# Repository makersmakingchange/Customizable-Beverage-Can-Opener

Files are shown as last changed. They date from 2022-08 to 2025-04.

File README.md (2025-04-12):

# Customizable Beverage Can Opener
The Customizable Beverage Can Opener is a beverage opening tool with different handle options for users with low strength and accuracy.

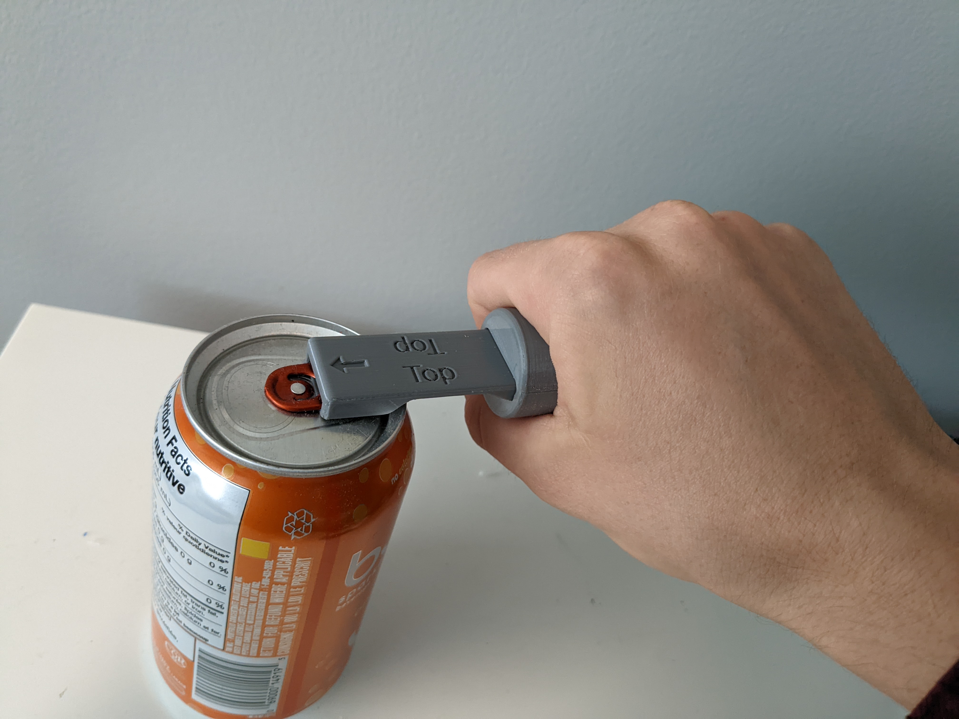
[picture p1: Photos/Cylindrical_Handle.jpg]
Picture of Customizable Beverage Can Opener.


## More info at
- [Makers Making Change Project Page](https://makersmakingchange.com/project/customizable-beverage-can-opener/)

## How to Obtain a Customizable Beverage Can Opener
### 1. Do it Yourself (DIY) or Do it Together (DIT)

This is an open-source assistive technology, so anyone is free to build it. All of the files and instructions required to build the Customizable Beverage Can Opener are contained within this repository. Refer to the Maker Checklist below.

### 2. Request a build of this device

If you would like to obtain a Customizable Beverage Can Opener, you may submit a build request through the [MMC Library Page](https://makersmakingchange.com/project/customizable-beverage-can-opener). The requestor is responsible for the cost of materials and any shipping.

### 3. How to build this device for someone else

If you have the skills and equipment to build this device, and would like to donate your time to create the switch for someone who needs it, visit the [MMC Maker Wanted](https://makersmakingchange.com/maker-wanted/) section.

## Getting Started

### 1. Read the Makers Checklist

The [Makers Checklist](Documentation/Customizable_Beverage_Can_Opener_Maker_Checklist_v1.0.pdf).

### 2. Print the 3D Printable components

Print the Base Can Opener and, optionally, any of the three handle designs.

All of the files and individual print files can be in the [/Build_Files/3D_Printing_Files](/Build_Files/3D_Printing_Files) folder.

### 3. Assemble the Customizable Berage Can Opener

Reference the [User Quick Guide](Documentation/Customizable_Beverage_Can_Opener_User_Guide_v1.0.pdf) for the tools and steps required to build each portion.

## Files
### Documentation
| Document             | Version | Link |
|----------------------|---------|------|
| Design Rationale     | 1.0     | [Customizable_Beverage_Can_Opener_Design_Rationale](/Documentation/Customizable_Beverage_Can_Opener_Design_Rationale_v1.0.pdf)     |
| Maker Checklist      | 1.0     | [Customizable_Beverage_Can_Opener_Maker_Checklist](/Documentation/Customizable_Beverage_Can_Opener_Maker_Checklist_v1.0.pdf)     |
| Bill of Materials    | 1.0     | [Customizable_Beverage_Can_Opener_Bill_of_Materials](/Documentation/Customizable_Beverage_Can_Opener_BOM_v1.0.csv)     |
| 3D Printing Guide    | 1.0     | [Customizable_Beverage_Can_Opener_3D_Printing_Guide](/Documentation/Customizable_Beverage_Can_Opener_3D_Print_Guide_v1.0.pdf)     |
| User Guide           | 1.0     | [Customizable_Beverage_Can_Opener_User_Guide](/Documentation/Customizable_Beverage_Can_Opener_User_Guide_v1.0.pdf)    |
| Changelog            | 1.0     | [Customizable_Beverage_Can_Opener_Changelog](/Documentation/Customizable_Beverage_Can_Opener_Changelog_v1.0.pdf)     |

### Design Files
[CAD Files](/Design_Files)

### Build Files
 - [3D Printing Files](/Build_Files/3D_Printing_Files)

## Attribution
Designers:
 - Idea for base can opener based on the design of pop-top can opener by Thingiverse User VegasGuy under the Creative Commons license - Attribution - Non-Commercial - No Derivatives.
 - Idea for Flat Handle based on Can Opener Helper by Pole Ergo under the Creative Commons license - Attribution - Non-Commercial - No Derivative.
 - Full Design by Neil Squire / Makers Making Change under license.
 - Documentation by Neil Squire / Makers Making Change.

## License
Everything needed or used to design, make, test, or prepare the Customizable Beverage Can Opener is licensed under the CERN 2.0 Permissive license <https://ohwr.org/project/cernohl/wikis/Documents/CERN-OHL-version-2> (CERN-OHL-P). 

<br /><span xmlns:dct="http://purl.org/dc/terms/" property="dct:title"><Device-Name></span> by <a xmlns:cc="http://creativecommons.org/ns#" href="www.makersmakingchange.com" property="cc:attributionName" rel="cc:attributionURL">Neil Squire</a> is licensed under a <a rel="license" href="http://creativecommons.org/licenses/by-sa/4.0/">Creative Commons Attribution-ShareAlike 4.0 International License</a>.

<!-- ABOUT MMC START -->
## About Makers Making Change
[Makers Making Change Logo](https://www.makersmakingchange.com/)

Makers Making Change is a program of [Neil Squire](https://www.neilsquire.ca/), a Canadian non-profit that uses technology, knowledge, and passion to empower people with disabilities.

Makers Making Change leverages the capacity of community based Makers, Disability Professionals and Volunteers to develop and deliver affordable Open Source Assistive Technologies.

 - Website: [www.MakersMakingChange.com](https://www.makersmakingchange.com/)
 - GitHub: [makersmakingchange](https://github.com/makersmakingchange)
 - Bluesky: [@makersmakingchange.bsky.social](https://bsky.app/profile/makersmakingchange.bsky.social)
 - Instagram: [@makersmakingchange](https://www.instagram.com/makersmakingchange)
 - Facebook: [makersmakechange](https://www.facebook.com/makersmakechange)
 - LinkedIn: [Neil Squire Society](https://www.linkedin.com/company/neil-squire-society/)
 - Thingiverse: [makersmakingchange](https://www.thingiverse.com/makersmakingchange/about)
 - Printables: [MakersMakingChange](https://www.printables.com/@MakersMakingChange)

### Contact Us
For technical questions, to get involved, or to share your experience we encourage you to [visit our website](https://www.makersmakingchange.com/) or [contact us](https://www.makersmakingchange.com/s/contact).
<!-- ABOUT MMC END -->

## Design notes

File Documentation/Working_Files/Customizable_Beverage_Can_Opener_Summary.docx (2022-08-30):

# Title

Customizable Beverage Can Opener

## Subtitle

Customizable tool to open beverage cans, with different handle options for users with low strength and accuracy.

## Device Specifications

Build Time:

< 1hr

1-4 hr

5-10hr

>10hr

Cost:

$0 - $10

$11 - $25

$26 - $50

$51 - $100

$101 - $250

$250+

Stage: Recently Added

Skills: 3D Printing

Need: Agility / Dexterity

Disability: Mobility/Physical

Difficulty: Beginner

License: Attribution-ShareAlike 4.0 International

Usages: Aids for Daily Living (ADL), Mobility

Designer: Neil Squire / Makers Making Change.

## Device Details

### Overview

The Customizable Beverage Can Opener provides a way for those with arthritis, low finger dexterity, low vision, or other related disabilities to open beverage cans with little strength or accuracy required. There are three different handles available for use with this device, hence the name “customizable”:

Base Can Opener:

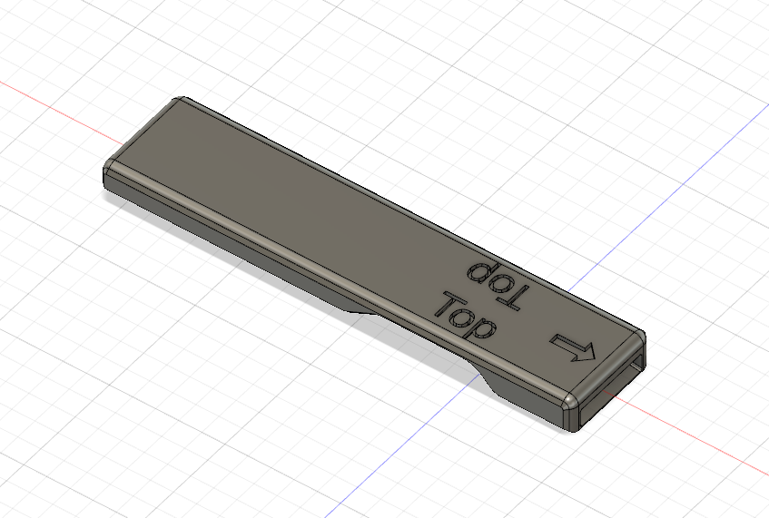
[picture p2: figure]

The Base Can Opener has a sloped hole which fits over almost all beverage can tabs. The device includes a graphic that describes which side should be facing upwards when opening the can and an arrow pointing towards the can opening. The device is designed to be used on its own or with the handle attached, as described below:

Cylindrical Handle

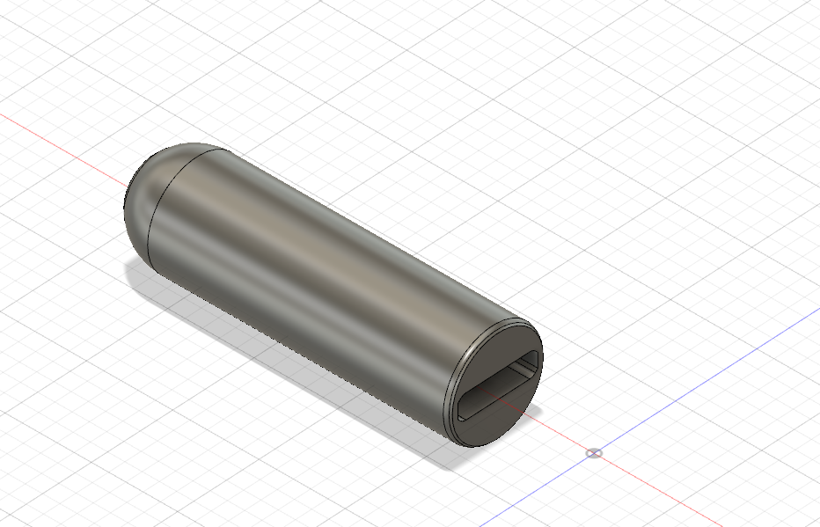
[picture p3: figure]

This handle is designed to fit the hand and is easy to grip for those with arthritis.

Flat Handle

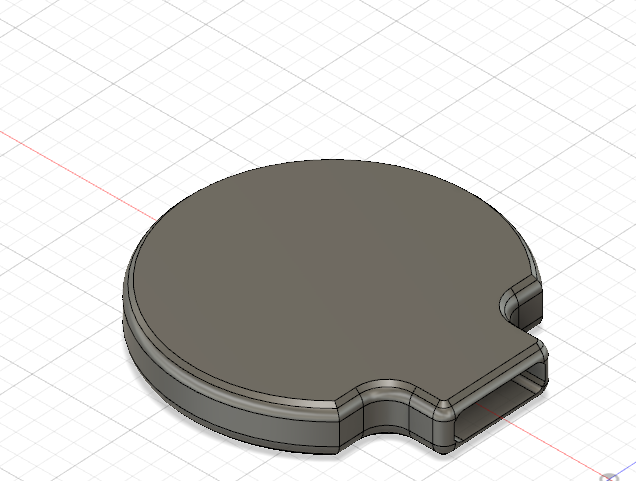
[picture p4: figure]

The Flat Handle is designed for someone with limited hand function and uses the wrist or elbow to open the can once the can opener is placed on the pull-tab.

Loop Handle

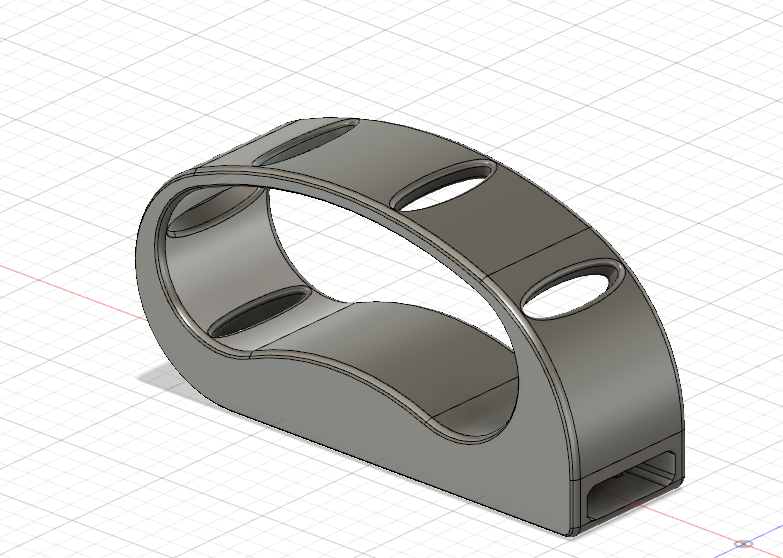
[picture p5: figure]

The Loop Handle is designed to open beverage cans without using fingers. The loop slides over the user’s hand, then the can opener can be used by lifting and twisting the hand.

### Similar Devices

- Another device for opening beverage cans which is much smaller and can be printed very quickly can be found here: https://makersmakingchange.com/project/beverage-can-opener/ (https://makersmakingchange.com/?post_type=project&p=15048&preview=true).
- A device intended for tin cans that require pulling back the entire metal lid, such as pet food, canned tuna or canned beans, is available here: https://makersmakingchange.com/project/pull-tab-tin-can-opener/ (https://makersmakingchange.com/?post_type=project&p=15035&preview=true).

### Cost

The total material cost for the base can opener and all three of the handles is approximately $2.50 CAD. The total cost for the base can opener and one of the handles is slightly over $1 CAD.

### Build Instructions

The base can opener can be attached to any of the handles by sliding the base can opener into the hole in the handle. If the fit is too loose, add super glue into the hole.

#### Skills Required

- 3D Printing

#### Time Required

- 3D Printing:
  - Base Can Opener: 1 hour.
  - Handle: 3-4 hours each.

#### Tools

Super glue or five-minute epoxy.

#### Components

- Base Can Opener
- Cylindrical Handle
- Flat Handle
- Loop Handle

#### 3D Printing

Full instructions can be found in the 3D Printing guide in the linked GitHub repository.

### Attribution

Idea for base can opener based on the design of pop-top can opener by Thingiverse User VegasGuy under the Creative Commons license - Attribution - Non-Commercial - No Derivatives.

Idea for Flat Handle based on Can Opener Helper by Pole Ergo under the Creative Commons license - Attribution - Non-Commercial - No Derivative.

Full Design by Neil Squire / Makers Making Change under license.

Documentation by Neil Squire / Makers Making Change.

© 2022 by Neil Squire / Makers Making Change This work is licensed under the CC BY SA 4.0 License: http://creativecommons.org/licenses/by-sa/4.0 Files available at https://makersmakingchange.com/project/customizable-beverage-can-opener/ Page 1 of 2

V1.0 | September 2022 Customizable Beverage Can Opener Summary

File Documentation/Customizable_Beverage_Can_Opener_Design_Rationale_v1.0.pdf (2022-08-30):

V1.0 | September 2022

## Customizable Beverage Can Opener

## DESIGN RATIONALE

© 2022 by Neil Squire / Makers Making Change This work is licensed under the CC BY SA 4.0 License: http://creativecommons.org/licenses/by-sa/4.0 Files available at https://makersmakingchange.com/project/customizable-beverage-can-opener/

## Introduction

Makers Making Change wanted to provide a tool for people with arthritis, low finger dexterity, or low vision to open beverage cans, and requiring only low strength and low accuracy to do so.

This device is not intended for tin cans that require pulling back the entire metal lid. For that, use this device https://makersmakingchange.com/project/pull-tab-tin-can-opener/. (https://makersmakingchange.com/?post_type=project&p=15035&preview=true)

## Requirements

Goals
G01 | To provide a way for people with low strength and accuracy to open the pull-tabs on beverage cans.
G02 | To provide a device cheaper than the commercial options.
G03 | To provide multiple handle options to accommodate different hand grips.
G04 | Work with both types of tabs (not just tabs with two holes– see Figure 1).
Functional Requirements
F01 Must not deteriorate with daily use.

Non-functional Requirement
NF01 All components must be 3D-printable with no supports.

Constraints
C01 Must be less than $5 to produce.

## Ideation

Since there are many open-source designs available for opening beverages, it did not seem necessary to re-design a new product. Several designs that used different methods to open cans seemed promising. The various designs and their pros and cons are listed below in the testing section.

One particular concern with some of the designs was the difference in pull tabs. Some tabs had two holes while others lack the top hole, which many can opener designs rely on.

## DESIGN RATIONALE

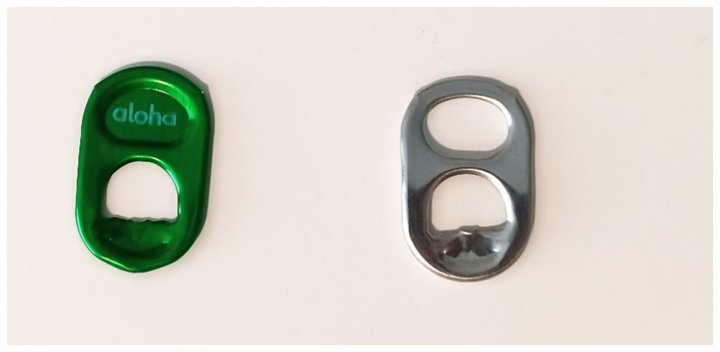
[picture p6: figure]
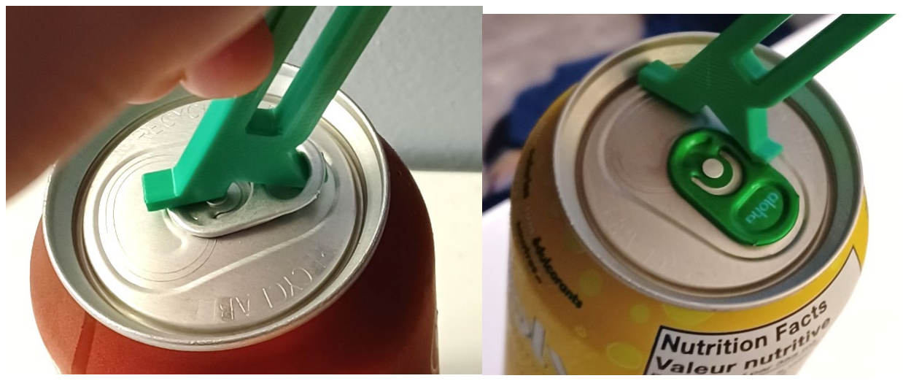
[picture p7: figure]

© 2022 by Neil Squire / Makers Making Change

Figure 1: An image showing the difference in Can Tabs. The bubly™ can tab (left) lacks a hole which the generic pop can has (right). Other commercial drinks such as RedBull™ Energy drink lack the top hole as well.

Figure 2: These 2 images demonstrate how a "hook-style" can opener cannot be used on a tab without a hole in the top.

## Testing

A variety of open-source designs for can-openers were printed and tested for ease-of-use, ease-of-printing, and functionality.

## DESIGN RATIONALE

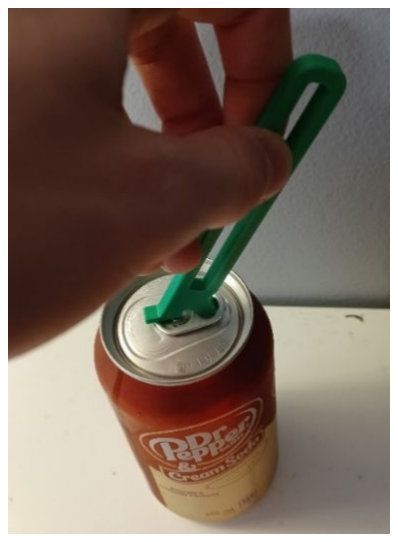
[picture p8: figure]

© 2022 by Neil Squire / Makers Making Change

Design 1: Jason from PrintLabs

Summary

This design uses a hook to grab the pull-tab using the top hole, then a levering action to open the can. The handle is large, easy to hold, and the device is overall effective and easy to use.

Pros

- Easy and very quick to print (no support,~0.5 hours)
- Uses very little filament (~5 grams)
- Easy to use, large handle, lots of leverage
Cons
- Does not work on pull-tabs with a single hole

## DESIGN RATIONALE

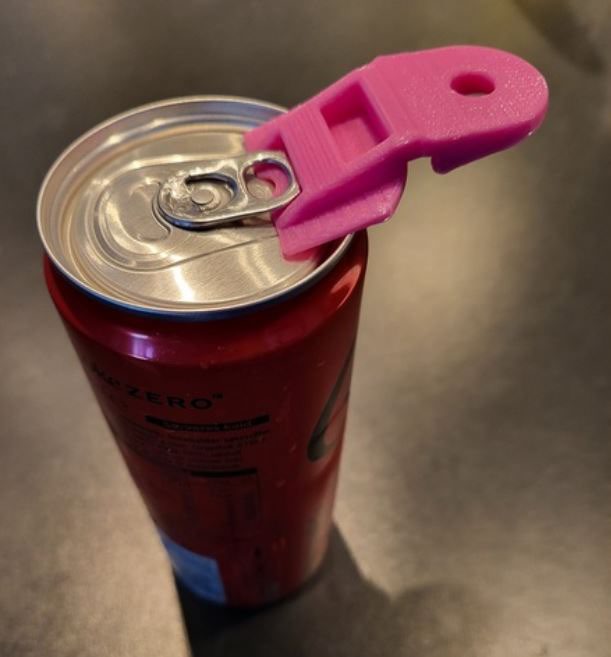
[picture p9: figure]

© 2022 by Neil Squire / Makers Making Change

Design 2: Can opener and lid by osund - Thingiverse (https://www.thingiverse.com/thing:5386671)

Summary

This is a small device which slides over the whole pull tab, allowing both tab styles to be opened. The small device size reduces print time and materials used. However, this comes at the expense of a difficult to hold and difficult to use device. This can opener also tends to slide off the tab during use, making for a somewhat frustrating experience overall.
Pros
- Very easy and quick to print (no supports, ~0.5 hours)
- Opens all styles of cans
- Slides over the pull-tab easily
- Also serves as a lid to protect drink from flies once opened Cons
- Not very easy to use as the device easily slides off the pull-tab
- Doesn’t give much leverage

## DESIGN RATIONALE

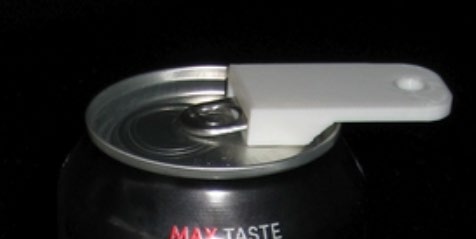
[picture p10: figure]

© 2022 by Neil Squire / Makers Making Change

Design 3: Pop Top Can Opener - Final by VegasGuy - Thingiverse (https://www.thingiverse.com/thing:3027499)

Summary

This device, like Design 2, slides over the whole pull-tab, allowing both tabs types to be opened. The Pop Top Can Opener is very small, making print time fast and uses less material, but is difficult to hold. However, this can opener is very effective, and for those with enough dexterity to hold the device, this Can Opener is probably the quickest and easiest to use on this list.
Pros
- Very easy and quick to print (no supports, ~0.5 hours)
- Opens all styles of cans
- Slides over pull-tab easily
- Easy to use, effectively opens cans Cons
- Handle is tiny; can be difficult to hold
- Design is closed for derivatives

## DESIGN RATIONALE

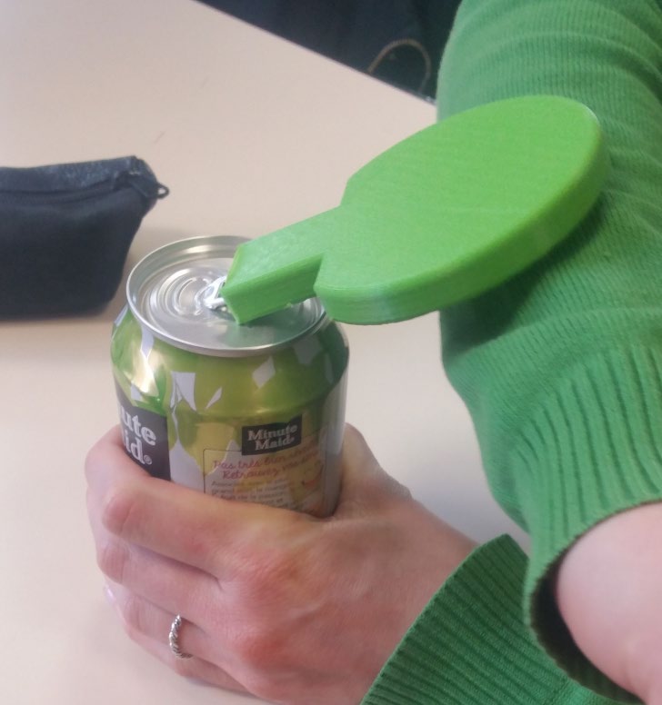
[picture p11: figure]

© 2022 by Neil Squire / Makers Making Change

Design 4: OT student project : Can opener helper by Pole_ergo - Thingiverse (https://www.thingiverse.com/thing:3846323)

Summary

The Can Opener Helper by Ergo Pole is different than the other designs. It includes an extra large, paddle-like surface to leverage a can open using the elbow or wrist. However, the design is flawed in that it doesn’t grip the can-tab well and easily slides off. This would be an easy modification, however this design is closed for derivatives.
Pros
- Opens all styles of cans
- Slides over pull-tab easily
- Provides Larger Handle (Not sure how beneficial this is) Cons
- Design is closed for derivatives
- Longer print time
- Doesn’t open cans as effectively as expected (reversible design makes can opener slide off)

## DESIGN RATIONALE

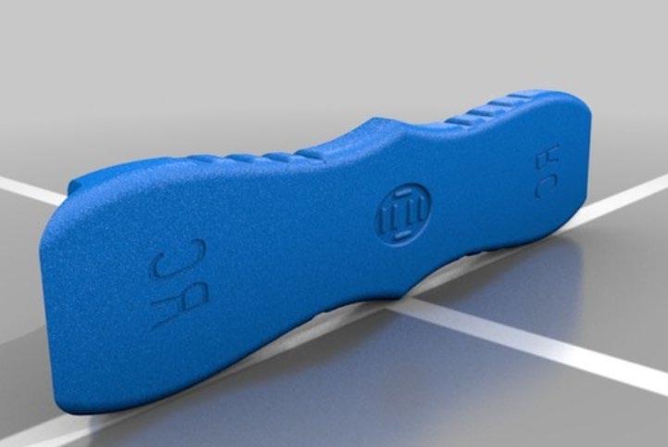
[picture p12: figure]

© 2022 by Neil Squire / Makers Making Change

Design 5: Soda Can Opener by ryancoretz - Thingiverse (https://www.thingiverse.com/thing:3697936)

Summary

This design works on both tab styles as it slides over the entire pull-tabs. The handle is nice to hold in the hand and the device easily and snugly slides over the pull-tab. However, this device often fails to open cans and instead bends the tab.
Pros
- Opens all styles of cans
- Slides over pull-tab easily
- Good size handle
- Double-sided
Cons
- Slightly longer print time (~1 hr)
- Will often bend tab instead of opening the can
- Does not reliably open generic pop cans

## Detailed Design

All the designs that were tested either did not work with the single hole pull tab or was not suitable for those with arthritis and low finger dexterity. As a result, a new base design was created based on the Pop-Top Can Opener by Thingiverse.com user Vegas Guy, (https://www.thingiverse.com/vegasguy/designs) as shown below:

## DESIGN RATIONALE

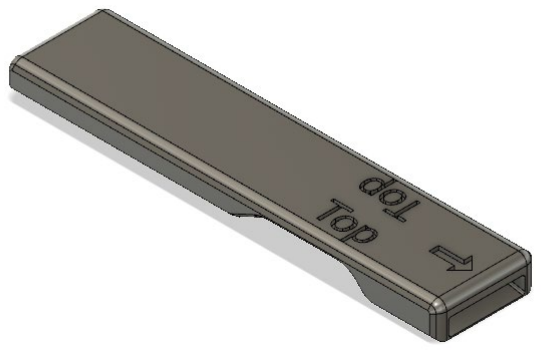
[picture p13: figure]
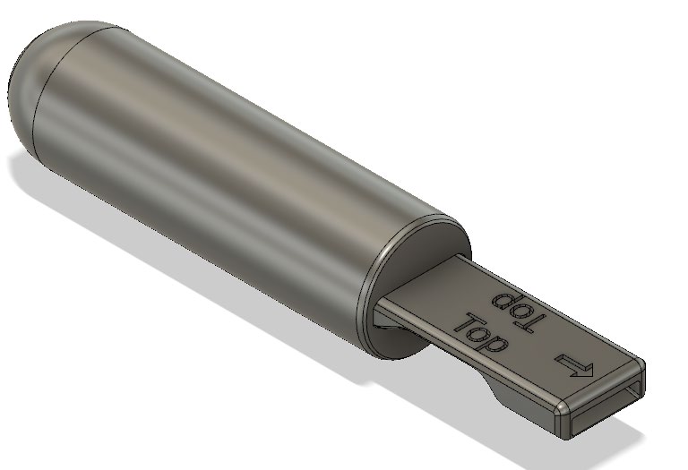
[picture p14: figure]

© 2022 by Neil Squire / Makers Making Change

The Base Can Opener has a sloped hole which fits over almost all beverage can tabs. The device includes a graphic that describes which side should be facing upwards when opening the can and an arrow pointing towards the can opening. The device is designed to be used on its own or with the handle attached, as described below:
Cylindrical Handle

The Cylindrical Handle is 30 mm in diameter and 100 mm long. This handle is designed to fit the shape of a hand and is easy to grip for those with arthritis.

## DESIGN RATIONALE

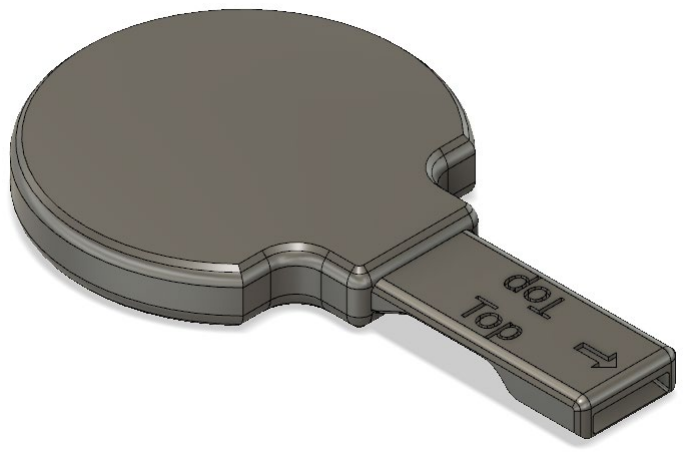
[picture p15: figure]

© 2022 by Neil Squire / Makers Making Change

Flat Handle

The Flat Handle is designed for someone with limited hand function and uses the wrist or elbow to open the can. The outside radius of the circle, which forms the body of the flat handle, is 39 mm. The thickness of this handle is 12.6 mm.

## DESIGN RATIONALE

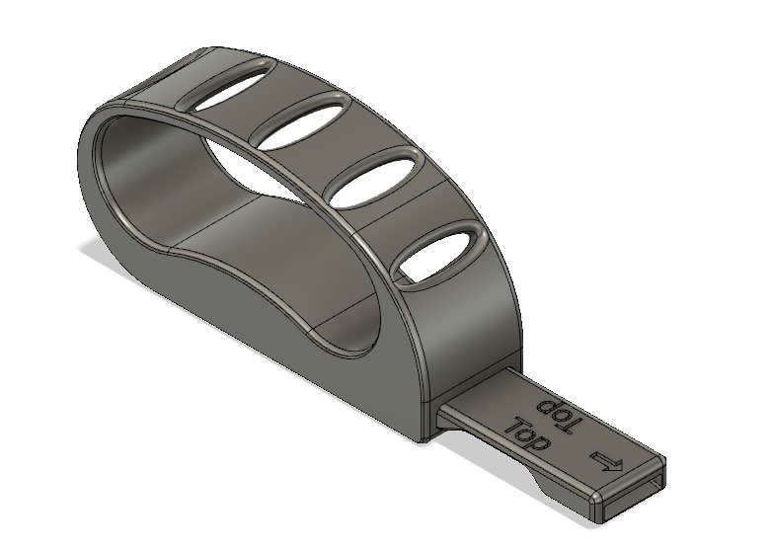
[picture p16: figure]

© 2022 by Neil Squire / Makers Making Change

Loop Handle

The Loop Handle provides a way to open beverage cans without using any fingers. With the loop over the user’s hand, and a lifting and twisting motion is used to open the can. Dimensions for the Loop Handle are shown below:

## DESIGN RATIONALE

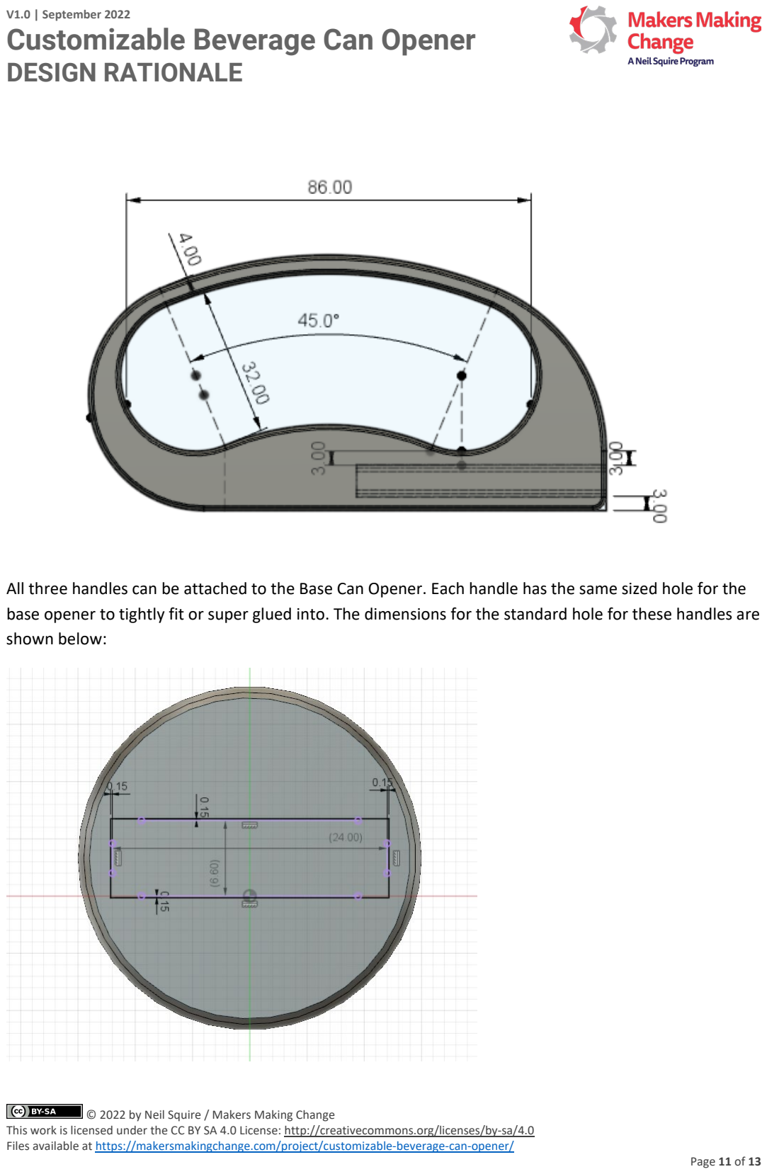
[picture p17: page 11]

© 2022 by Neil Squire / Makers Making Change

All three handles can be attached to the Base Can Opener. Each handle has the same sized hole for the base opener to tightly fit or super glued into. The dimensions for the standard hole for these handles are shown below:

## DESIGN RATIONALE

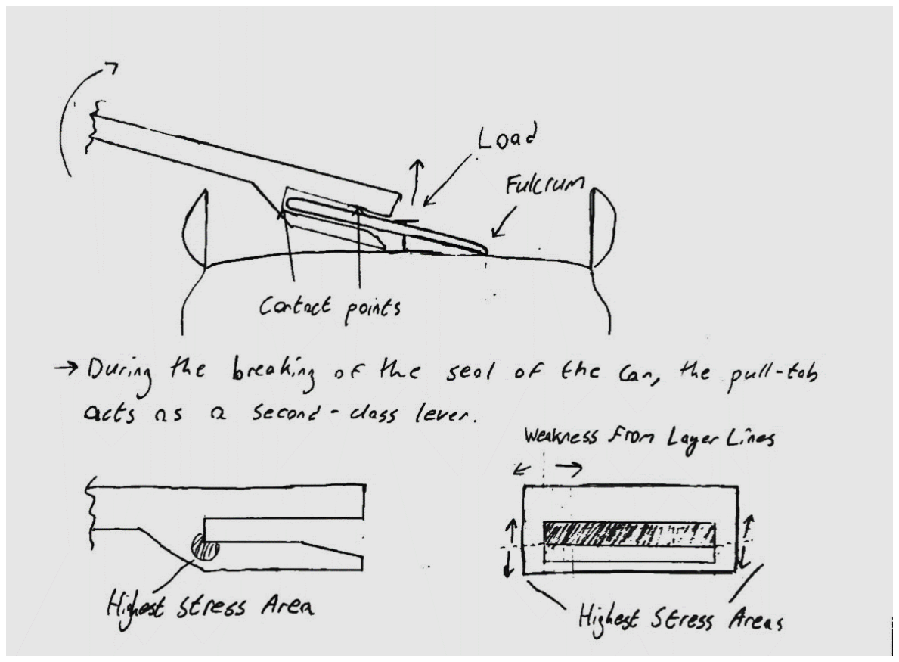
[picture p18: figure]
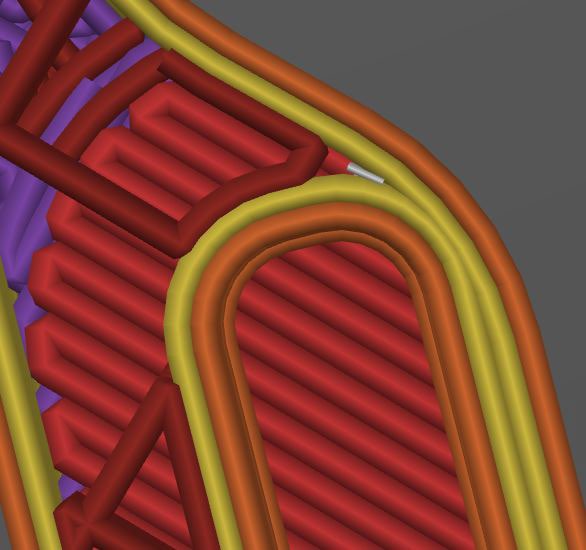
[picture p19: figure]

© 2022 by Neil Squire / Makers Making Change

Each handle hole is the same size as the handle of the base can opener, which has a width of 24 mm, a height of 6.6 mm, plus a 0.15 mm clearance. Both the handle and the standard holes have a length of 53 mm.

Free Body Diagram

This free-body diagram shows the concentration of stress in the bottom left corner drawing. To relieve some of this stress, a fillet was added. Enough space for four 0.4 mm perimeter lines was given to this area, as shown in the picture below:

## DESIGN RATIONALE

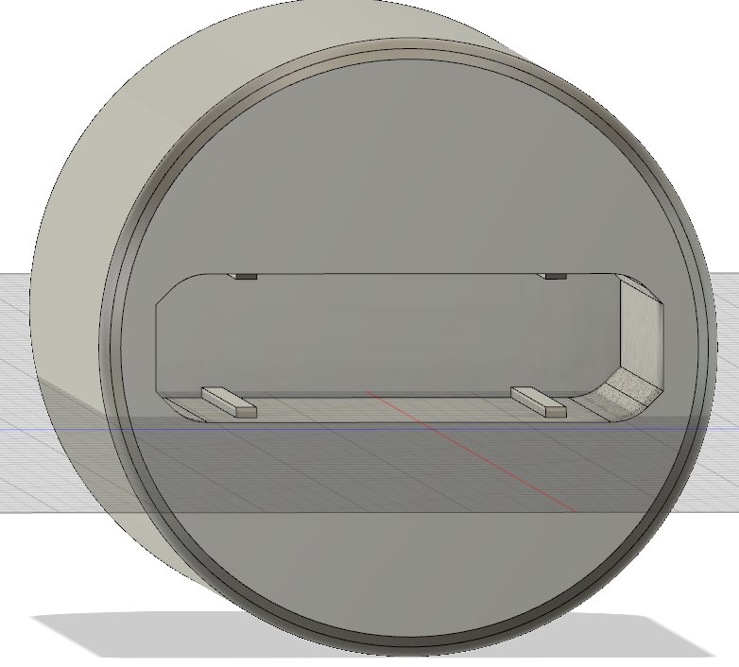
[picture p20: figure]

© 2022 by Neil Squire / Makers Making Change

Print Orientation
The Base Can Opener was tested by printing it on its largest face and on its side (or the non-rectangular face). Printing on its side ensures that the surface contacts the pull-tab, is easily inserted onto the tab, and that the tab does not get caught between the layer lines. Additionally, this print orientation ensures that the force from opening the can does not get applied in the direction of the layer lines, as shown in the free-body diagram above.

Crush Ribs

Crush ribs were added to the inside of all the handles to ensure a tight fit and plenty of tolerance for variations between different printers. The crush ribs are 0.5 mm tall and 1 mm wide. They start a small distance from the hole and have a chamfer so that the handle slides in easily.

## Opportunities for Improvement

- Having two parts that fit together may be a problem that could be solved with a later iteration.

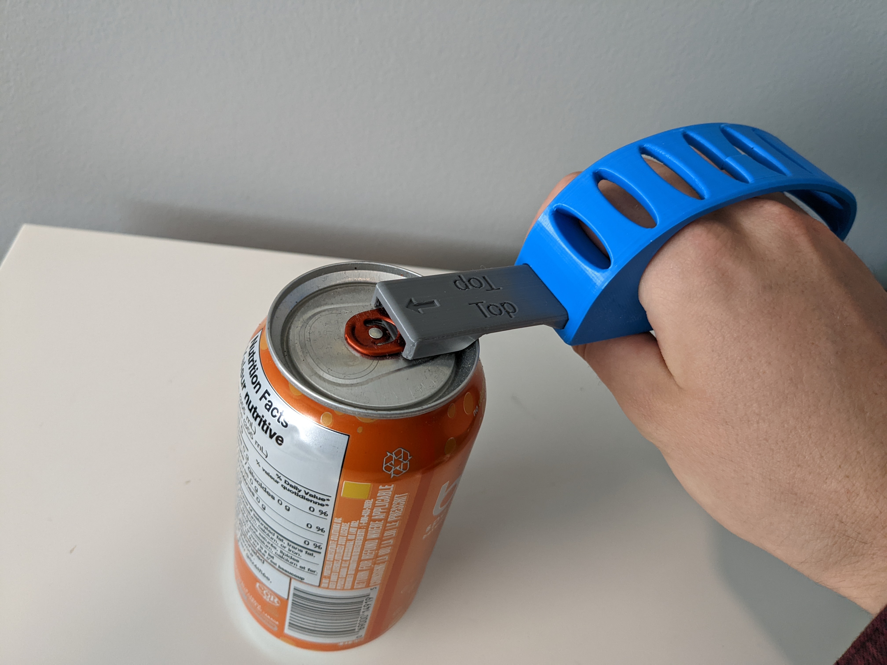
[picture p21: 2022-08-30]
Photos/Loop_Handle.jpg

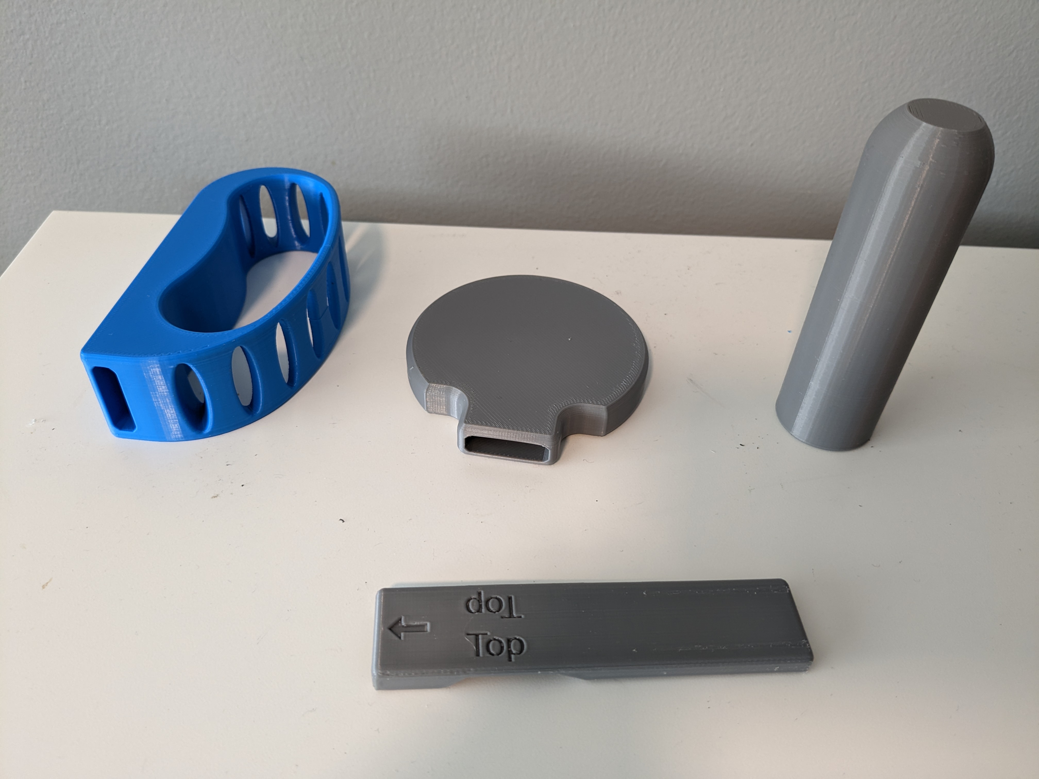
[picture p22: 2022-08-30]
Photos/All_Handles_and_Base.jpg

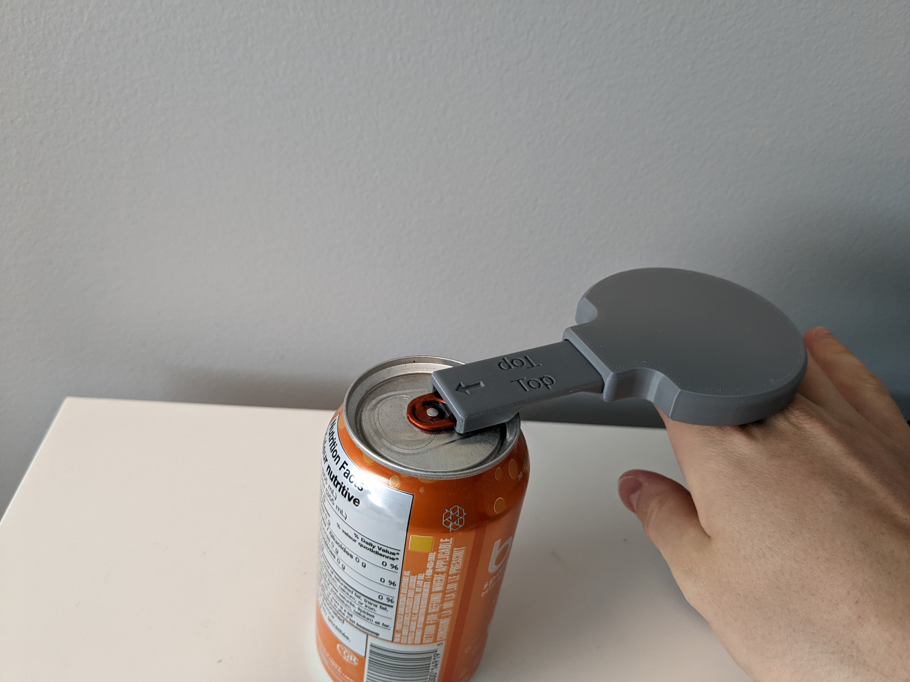
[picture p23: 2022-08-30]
Photos/Flat_Handle.jpg

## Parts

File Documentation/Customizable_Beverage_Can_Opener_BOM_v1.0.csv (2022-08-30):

Device: Customizable Can Opener |  | Total Cost | Total Print time (hr) | Total filament (g)
Version: V1.0 | Date Created: 9/01/2021 | $2.53 | 1.17 | 9
3D Printed Parts ESTIMATED PRICING USING 1KG ROLL COST: | $25.00
Part | Description | Quantity Needed | TOTAL Mass (g) | Estimated Price | Print Time (Min) | Link
Base_Can_Opener.stl | The fully functional can opener without extra handle. | 1 | 9 | $0.23 | 70 | Add GitHub Link when complete
Cylindrical_Handle.stl | A cylindrical handle designed for those with arthritis. | 1 | 27 | $0.68 | 190 | Add GitHub Link when complete
Flat_Handle.stl | A flat, larger handle for those with low dexterity. | 1 | 29 | $0.73 | 143 | Add GitHub Link when complete
Loop_Handle.stl | A handle with a hand shaped loop for a user to slide their hand through. | 1 | 36 | $0.90 | 264 | Add GitHub Link when complete
 |  |  | Total Print Cost: | $2.53

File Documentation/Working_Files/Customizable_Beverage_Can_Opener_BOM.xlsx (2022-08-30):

Device: Customizable Can Opener |  | Total Cost | Total Print time (hr) | Total filament (g)
Version: V1.0 | Date Created: 9/01/2021 | $2.52 | 1.17 | 9
3D Printed Parts ESTIMATED PRICING USING 1KG ROLL COST: | $25.00
Part | Description | Quantity Needed | TOTAL Mass (g) | Estimated Price | Print Time (Min) | Link
Base_Can_Opener.stl | The fully functional can opener without extra handle. | 1 | 9 | $0.22 | 70 | https://github.com/makersmakingchange/customizable-beverage-can-opener/blob/main/Build_Files/3D_Printing_Files/Base_Can_Opener.stl
Cylindrical_Handle.stl | A cylindrical handle designed for those with arthritis. | 1 | 27 | $0.68 | 190 | https://github.com/makersmakingchange/customizable-beverage-can-opener/blob/main/Build_Files/3D_Printing_Files/Cylindrical_Handle.stl
Flat_Handle.stl | A flat, larger handle for those with low dexterity. | 1 | 29 | $0.73 | 143 | https://github.com/makersmakingchange/customizable-beverage-can-opener/blob/main/Build_Files/3D_Printing_Files/Flat_Handle.stl
Loop_Handle.stl | A handle with a hand shaped loop for a user to slide their hand through. | 1 | 36 | $0.90 | 264 | https://github.com/makersmakingchange/customizable-beverage-can-opener/blob/main/Build_Files/3D_Printing_Files/Loop_Handle.stl
 |  |  | Total Print Cost: | $2.52

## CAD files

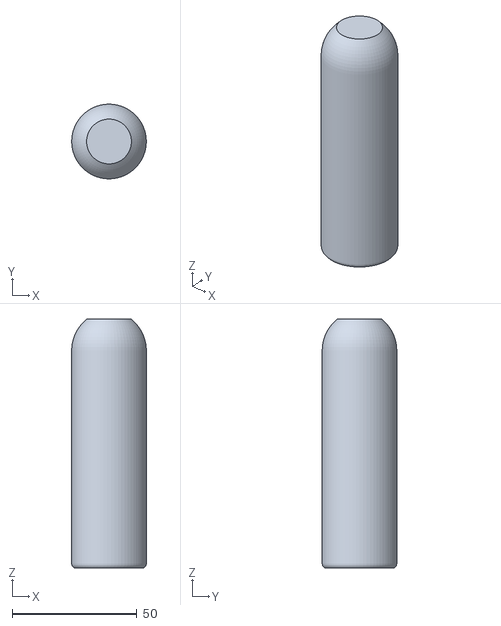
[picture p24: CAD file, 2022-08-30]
Build_Files/3D_Printing_Files/Cylindrical_Handle.stl
30.0 x 30.0 x 100.0

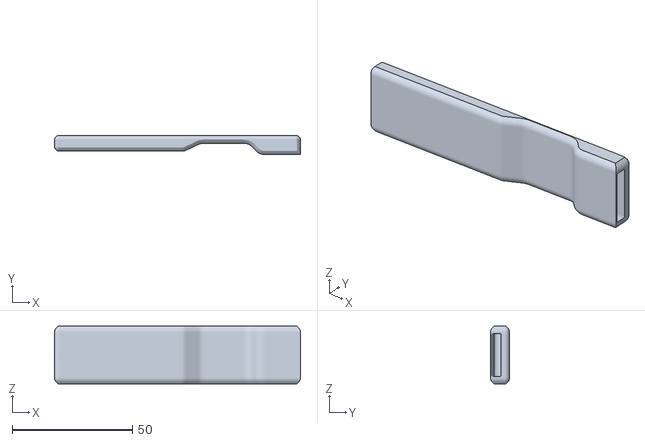
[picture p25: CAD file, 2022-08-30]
Build_Files/3D_Printing_Files/Base_Can_Opener.stl
102.4 x 8.00 x 24.0

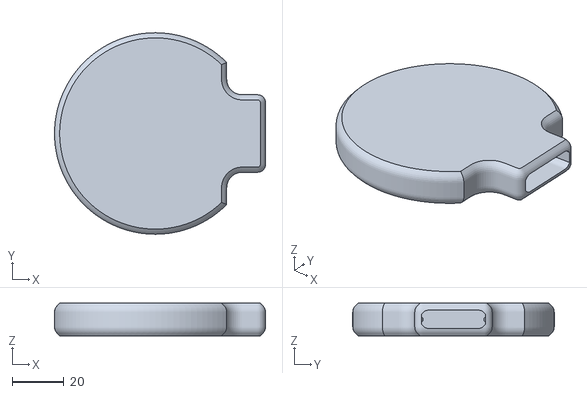
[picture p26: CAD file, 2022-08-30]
Build_Files/3D_Printing_Files/Flat_Handle.stl
81.7 x 78.0 x 12.6

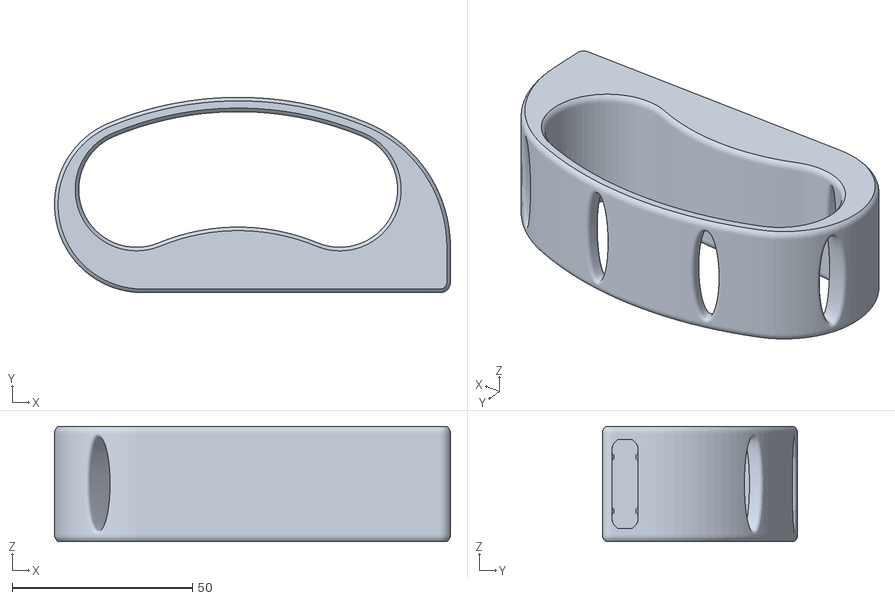
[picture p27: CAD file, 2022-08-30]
Build_Files/3D_Printing_Files/Loop_Handle.stl
109.9 x 54.2 x 32.0

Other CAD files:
Design_Files/CAD_Files/Customizable_Beverage_Can_Opener.f3d

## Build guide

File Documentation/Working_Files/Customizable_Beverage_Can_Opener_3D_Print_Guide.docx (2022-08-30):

# 3D Printing Summary

Metrics | Base Can Opener Only | With Cylindrical Handle | With Flat Handle | With Loop Handle
Total Print Time (min) | 69 | 267 | 213 | 317
Total Number of Components | 1 | 2 | 2 | 2
Typical Total Mass (g) | 9 | 37 | 38 | 46
Typical Number of Print Setups | 1 | 1 | 1 | 1

# 3D Printing Settings

Print File Name | Qty | Total Print Time (hr:min) | Mass (g) | Infill (%) | Support | Layer Height/ Nozzle Diameter (mm) | Notes (orientation, special settings, etc.)
Base_Can_Opener.stl | 1 | 1:09 | 9 | 20 | No Support | 0.2/0.4 | - Must have at least 2 perimeters. - Must orient on its side, so that the non-rectangular face is laying on the print bed.
Cylindrical_Handle.stl | 1 | 3:19 | 28 | 20 | No Support | 0.2/0.4 | - Must have at least 2 perimeters. - Orient upright so that the hole for the handle is on the print bed.
Flat_Handle.stl | 1 | 2:24 | 29 | 20 | No Support | 0.2/0.4 | - Must have at least 2 perimeters. - Must orient so that either flat side is on the print bed.
Loop_Handle.stl | 1 | 4:08 | 37 | 20 | No Support | 0.2/0.4 | - Must have at least 2 perimeters. - Orient so that the handle is on its side.

# Post-Processing

- Remove any burrs or sharp edges if needed.
- Super glue can be added to attach the can opener socket to the handle socket if desired.

# Examples of Quality Prints

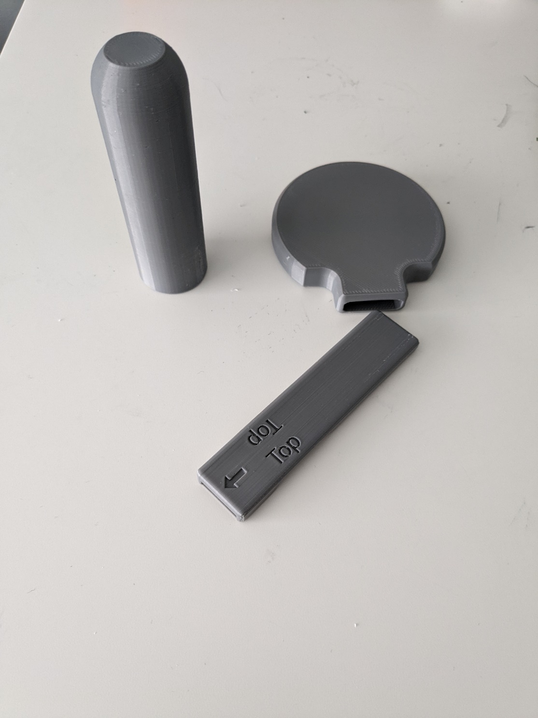
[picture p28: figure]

© 2022 by Neil Squire / Makers Making Change This work is licensed under the CC BY SA 4.0 License: http://creativecommons.org/licenses/by-sa/4.0 Files available at https://makersmakingchange.com/project/customizable-beverage-can-opener/ Page 1 of 2

V1.0 | September 2022 Customizable Beverage Can Opener 3D Printing Guide

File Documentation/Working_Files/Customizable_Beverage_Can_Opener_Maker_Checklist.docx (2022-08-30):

# Maker To Do List

- Read the Summary for information about the available handle options and similar devices.
- Talk with the user about the available options and determine which handle or which can opener is best suited to their needs.
- 3D print device.
- Glue handle to device if needed using cyanoacrylate glue or five-minute epoxy.
- Test device.
- Print User Guide.

# Items to Give to User

- Printed, tested device.
- User Guide

© 2022 by Neil Squire / Makers Making Change This work is licensed under the CC BY SA 4.0 License: http://creativecommons.org/licenses/by-sa/4.0 Files available at https://makersmakingchange.com/project/customizable-beverage-can-opener/ Page 1 of 1

V1.0 | September 2022 Customizable Beverage Can Opener Maker Checklist

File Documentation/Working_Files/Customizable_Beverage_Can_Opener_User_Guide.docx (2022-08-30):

## Introduction

The Customizable Beverage Can Opener provides a way for people with arthritis, low finger dexterity, or low vision to open beverage cans, while requiring only low strength or accuracy. The “customizable” refers to the three handles which can be used with the same base can opener. The handles provide support for opening beverage cans in different ways.

## Features

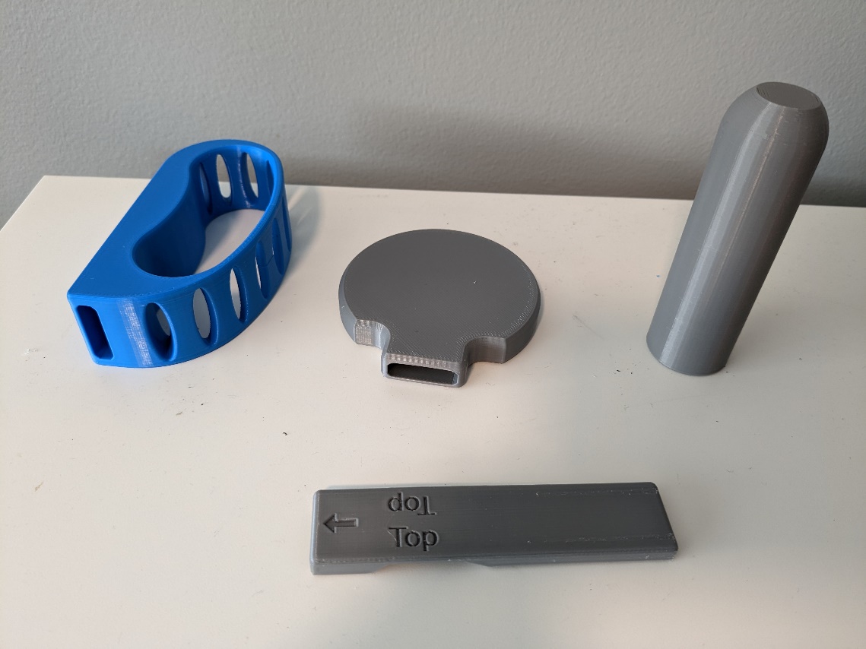
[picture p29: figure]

1. Loop Handle: Allows user to loop the can opener over their hand as they open the can.
2. Flat Handle: Allows the user to use their wrist or arm to lift the pull tab
3. Cylindrical Handle: Provides the user with an ergonomic grip which can be easily held by those with arthritis.
4. Base Can Opener: The part of the can opener which attaches to the can pull tab. The Base Can Opener can be used alone or with any of the three handles.

## Usage

Step 1: Slide the Base Can Opener into the handle of choice.

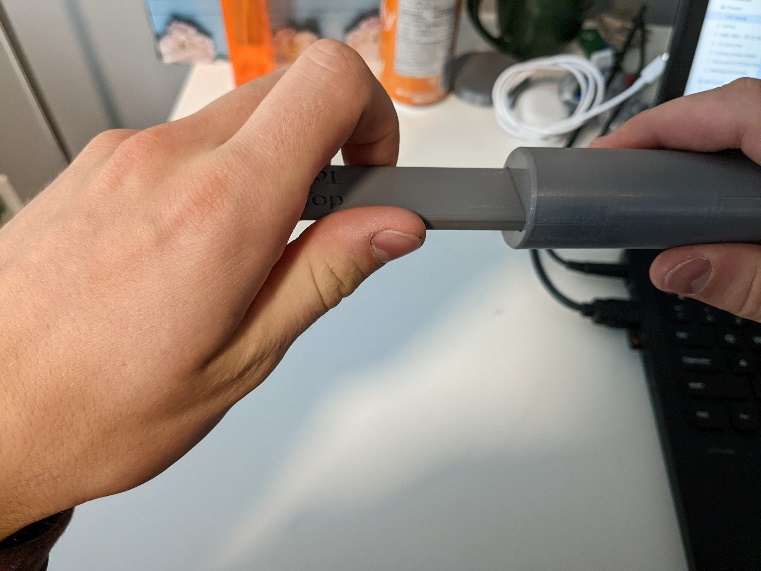
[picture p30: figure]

Step 2: Slide the Can Opener over the pull-tab of your canned beverage and lift upwards to open the can.

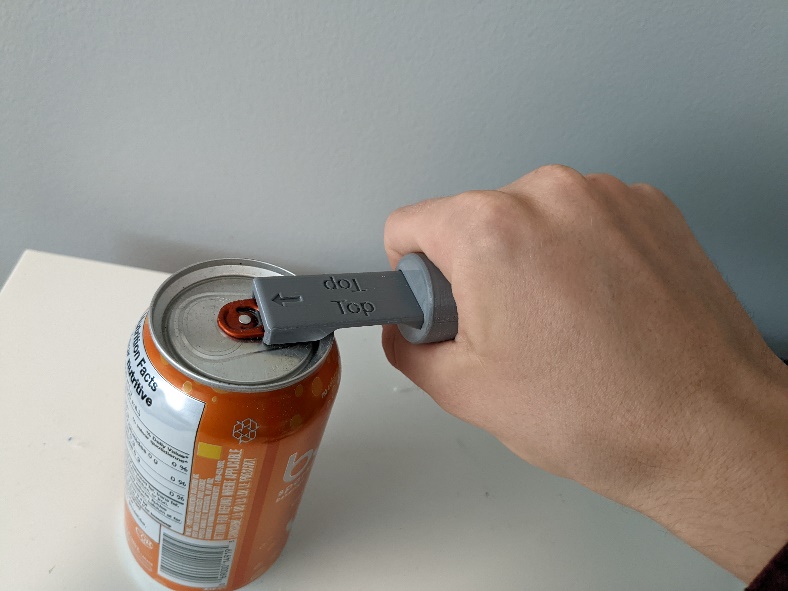
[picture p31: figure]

Compatibility

The Customizable Beverage Can Opener is compatible with any aluminum beverage can with a pull-tab.

## Cleaning

Wipe with sterilizing cloth or use sterilizing spray. Do not expose to high heat or dishwasher.

© 2022 by Neil Squire. This work is licensed under the CC BY SA 4.0 License: http://creativecommons.org/licenses/by-sa/4.0 Files available at https://makersmakingchange.com/project/customizable-beverage-can-opener/ Page 2 of 3

V1.0 | September 2022 Customizable Beverage Can Opener user Quick Guide

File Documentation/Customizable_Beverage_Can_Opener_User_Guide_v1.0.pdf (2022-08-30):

V1.0 | September 2022

# Customizable Beverage Can Opener

## USER QUICK GUIDE

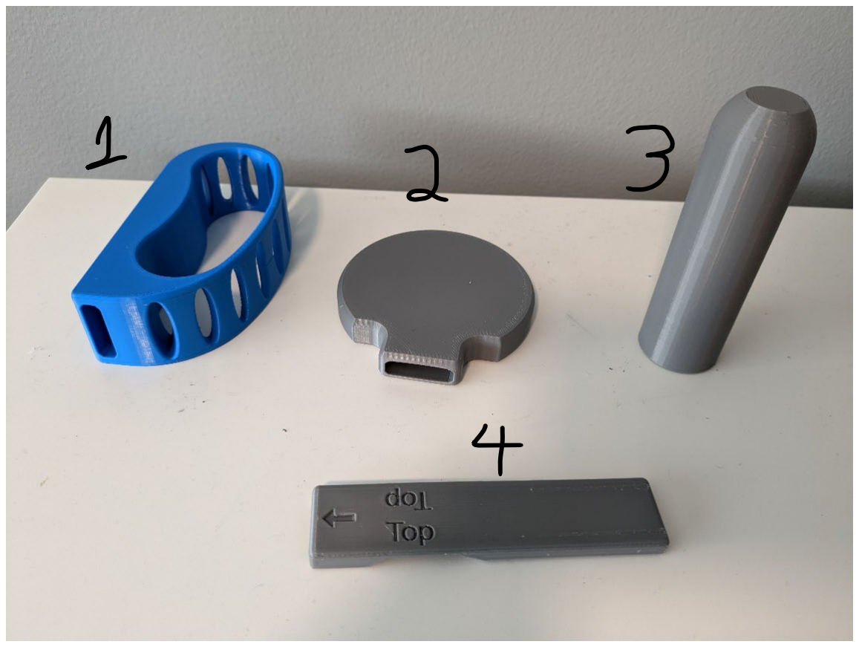
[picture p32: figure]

© 2022 by Neil Squire. (https://neilsquire.ca/)
This work is licensed under the CC BY SA 4.0 License: http://creativecommons.org/licenses/by-sa/4.0 Files available at https://makersmakingchange.com/project/customizable-beverage-can-opener/

Introduction
The Customizable Beverage Can Opener provides a way for people with arthritis, low finger dexterity, or low vision to open beverage cans, while requiring only low strength or accuracy. The “customizable” refers to the three handles which can be used with the same base can opener. The handles provide support for opening beverage cans in different ways.
Features
1. Loop Handle: Allows user to loop the can opener over their hand as they open the can.

### 2. Flat Handle: Allows the user to use their wrist or arm to lift the pull tab

3. Cylindrical Handle: Provides the user with an ergonomic grip which can be easily held by those with arthritis.
4. Base Can Opener: The part of the can opener which attaches to the can pull tab. The Base Can Opener can be used alone or with any of the three handles.

V1.0 | September 2022

# Customizable Beverage Can Opener

## USER QUICK GUIDE

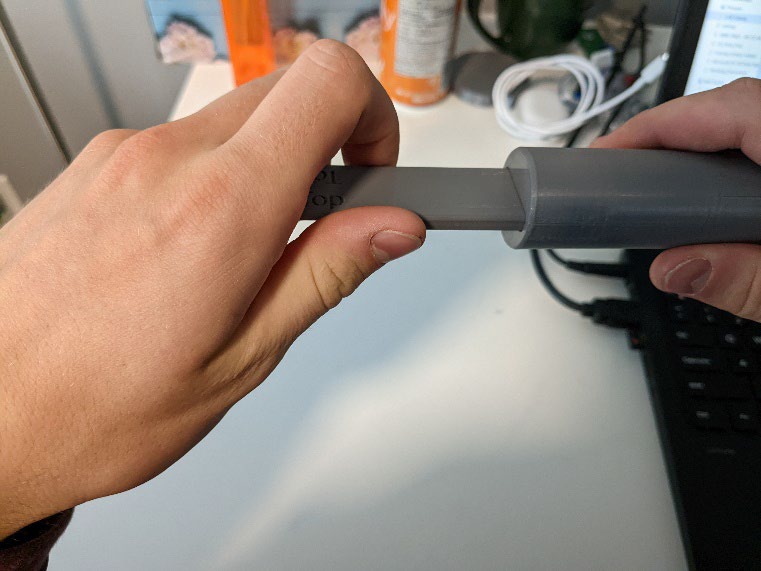
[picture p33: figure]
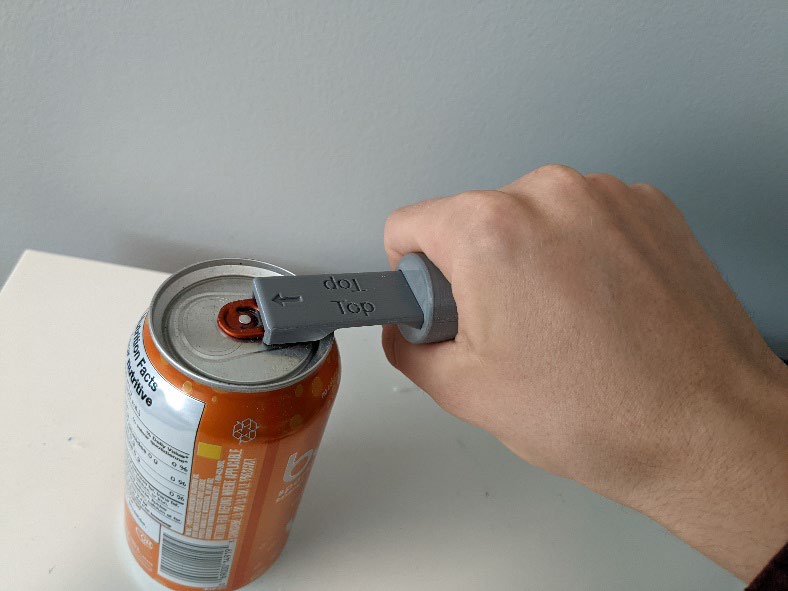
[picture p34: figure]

© 2022 by Neil Squire. (https://neilsquire.ca/)
This work is licensed under the CC BY SA 4.0 License: http://creativecommons.org/licenses/by-sa/4.0 Files available at https://makersmakingchange.com/project/customizable-beverage-can-opener/

Usage
Step 1: Slide the Base Can Opener into the handle of choice.
Step 2: Slide the Can Opener over the pull-tab of your canned beverage and lift upwards to open the can.

Compatibility

The Customizable Beverage Can Opener is compatible with any aluminum beverage can with a pull-tab. Cleaning
Wipe with sterilizing cloth or use sterilizing spray. Do not expose to high heat or dishwasher.

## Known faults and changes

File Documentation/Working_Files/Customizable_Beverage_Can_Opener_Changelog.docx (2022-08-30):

# Version 1.0 | Date 06/20/2022

- New Design based on Pop Top Can Opener - Final by VegasGuy - Thingiverse (https://www.thingiverse.com/thing:3027499) and OT student project : can opener helper / aide à l'ouverture de cannettes by Pole_ergo - Thingiverse (https://www.thingiverse.com/thing:3846323).
- Documentation by Neil Squire / Makers Making Change.

© 2022 by Neil Squire / Makers Making Change This work is licensed under the CC BY SA 4.0 License: http://creativecommons.org/licenses/by-sa/4.0 Files available at https://makersmakingchange.com/project/customizable-beverage-can-opener/ Page 1 of 1

V1.0 | September 2022 Customizable Beverage Can Opener changelog
